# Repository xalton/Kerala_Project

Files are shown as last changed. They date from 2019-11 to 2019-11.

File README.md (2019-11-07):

# __PROJECT : refrigerant backpack__
*Team: Claire Chavigny, Carla Debarre, Ibrahim Khaled, Louise Gorioux*

> *A Myco-material backpack respecting the cold chain capable of carrying vaccines, allowing doctors to act while on the move to reach as many people as possible.*

## Project summary :

After many researches on the web, discussion with Indians, people from the medical sphere, our professors  and reflexions within our groupe, the project consists of a backpack capable of transporting vaccines, in an appropriate environment (2°- 8°C) over a six-hour period. Following the floods in India during last summer, poor healthcare has developed in the camps and diseases are spreading quickly. Moreover, if inhabitants want to be vaccinated they need to go to hospitals which are crowded in those moments. The project would be used during the camp period when infections are most common but also in everyday life to increase the impact of vaccination. 

The goal is to stop the spread of infection, reaching as many people as possible by giving them the opportunity to be immunized, thanks to the doctors on the field. Furthermore it will avoid the overload in hospitals. The project acts as a prevention in the camps after the disaster . The project aims to be more innovative than a cooling box by creating a myco-material refrigerant backpack. 

After several prototypes, tests and questioning, (cfr: process) we developed a backpack in polystyrene to find the best shape for the back and its thermal resistance (the ratio between thickness and thermal conductivity). In the bag stands a wood composite box (270mmx200mmx440mm) in which the 1O5 vaccines are located. Around the box are placed the eutectic plates. An unique assembly of straps is using all around the bag (it’s possible to use recovery material). 

The mycelium and the polystyrene have similarities regarding the thermal conductivity. It brings lightness to the bag. (cfr process).
To carry on our project, the backpack will be made by mycelium, which is the mushroom’s seed that could be developed by themselves. Thanks to it and the addition of substrate as sawdust, we are able to manufacture the material, called myco-material, biodegradable and one hundred percent ecological. For the development of the myco-material,  a cardboard mold’s need to be produced with the laser, as well as the box containing vaccines, from a file that we have made. 

The myco-material produces ten times lower carbon dioxide and uses eight times lower energy than the production of polystyrene foam. Its thermal conductivity is good enough to make it a good insulator completely ecological and biodegradable compared to polystyrene.

Concerning the production, Kerala arranges 22 fablabs and 3000 camps (disaster in august 2018) have taken their seats through the state. Furnishing two bags (210 vaccines) per camp means that every fablab should provide 270 bags. The web of fablabs in Kerala being dispersed, it would help us to send the bags to the various hospitals around. 

Regarding the time of production, we calculate that we need 5h beside the 30 days of myco-materials culture. The price of the bag is approximately 30 euros and total weights is 3.7kg.

We approached this project through the healthcare problem, that seemed important to all of us. There are many things still to be improved and we hope it will give idea and motivation to the NGO to develop a better version of it. We also wanted to enhance the agricultural crop by  using mushrooms and promoting innovative way of building that take care of the environnement. 

##  Storyboard :

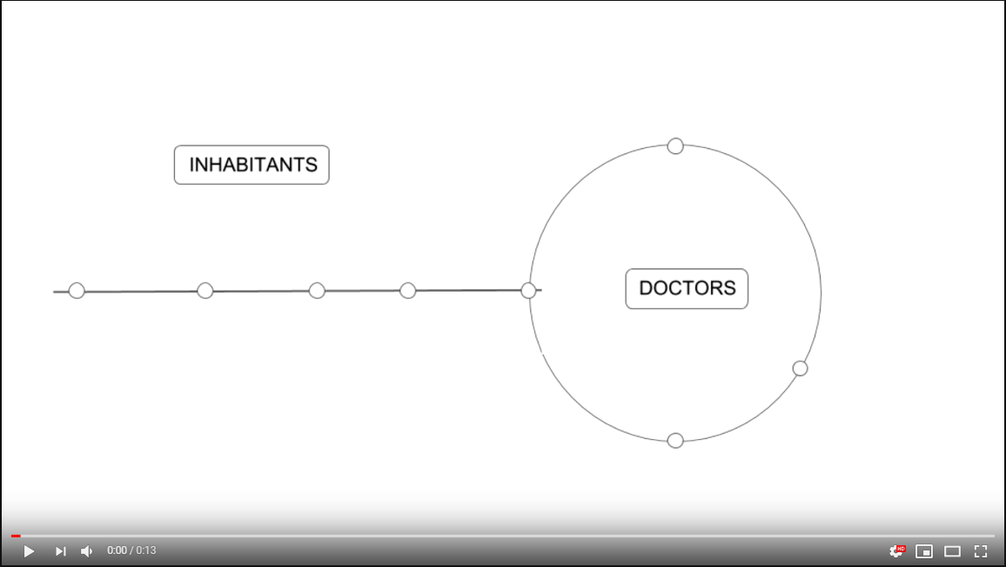
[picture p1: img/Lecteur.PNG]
Storyboard (https://youtu.be/2fGu3O8SxWQ)


##  Final prototype: 

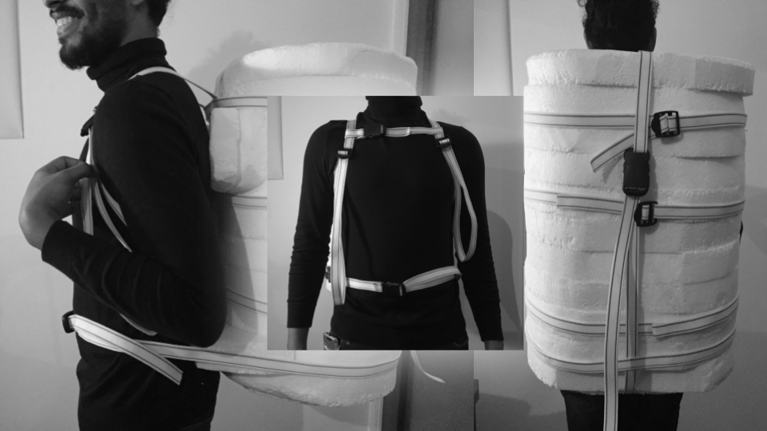
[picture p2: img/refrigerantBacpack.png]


## Tutorial :
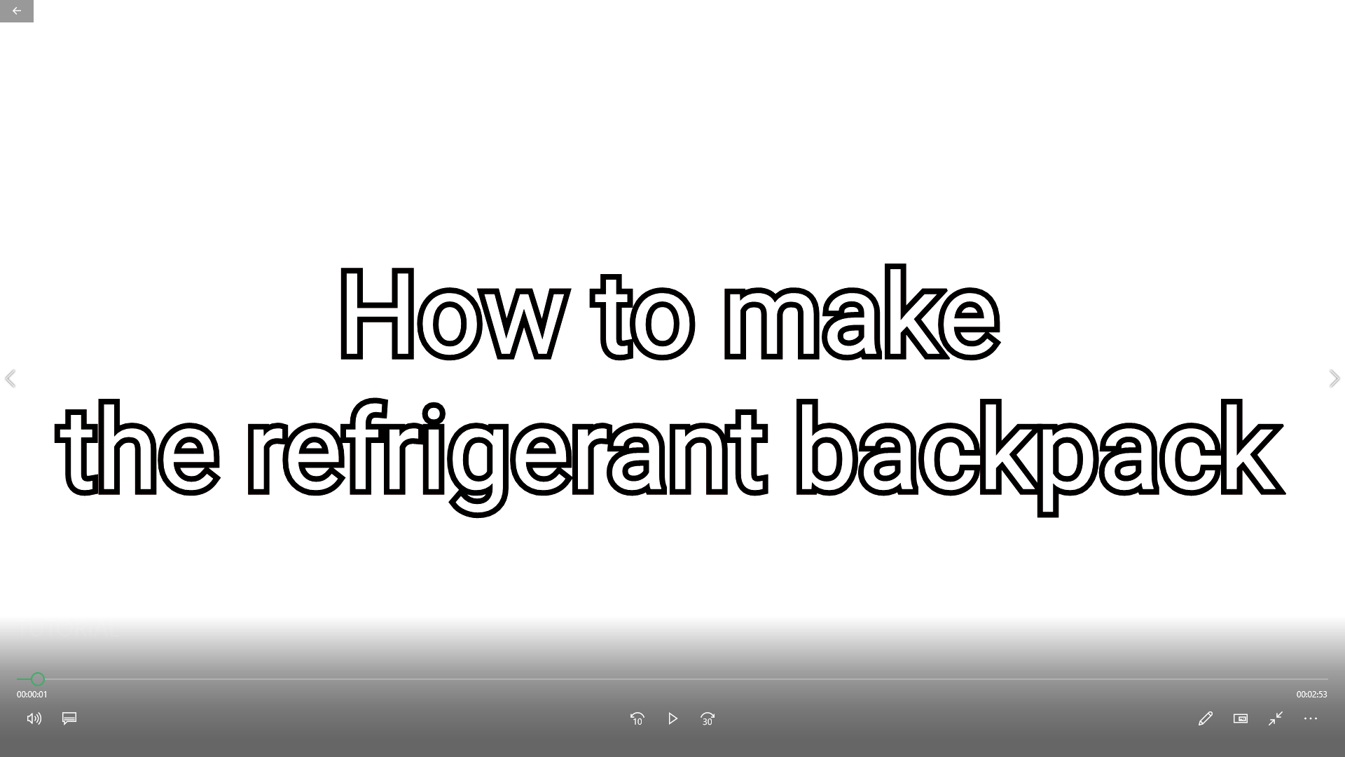
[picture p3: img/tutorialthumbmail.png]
tuto (https://youtu.be/IbsIk9dsDAU)


##  Bibliography :
- Contacts:
	- Pauline Kennes and Catherine Bachy at DWB Belgium

	- Michäël Gäthögö at DWB

	- Prithvi helped us as a local inhabitant
- Links:
	- [http://www.who.int/immunization/programmes_systems/supply_chain/optimize/Cooling_17july12.pdf](http://www.who.int/immunization/programmes_systems/supply_chain/optimize/Cooling_17july12.pdf)

	- [https://www.cdc.gov/vaccines/recs/storage/downloads/emergency-transport.pdf](https://www.cdc.gov/vaccines/recs/storage/downloads/emergency-transport.pdf)

	- [https://www.permafungi.be/projet/](https://www.permafungi.be/projet/)

	- [https://www.mediamatic.net/en/page/69393/mycelium-theorists-scientists](https://www.mediamatic.net/en/page/69393/mycelium-theorists-scientists)

	-	https://emergency.unhcr.org

	-	[https://motherboard.vice.com/en_us/article/pgazx8/the-house-that-spores-built](https://motherboard.vice.com/en_us/article/pgazx8/the-house-that-spores-built)

	-	[http://www.mycoworks.com/](http://www.mycoworks.com/)

	-	[http://ecovativedesign.com/](http://ecovativedesign.com/)

	-	[https://www.irit.fr/neocampus/images/stages/2018/Balthazar-Lesmie_Stage.pdf](https://www.irit.fr/neocampus/images/stages/2018/Balthazar-Lesmie_Stage.pdf)
	-   [http://www.cg43.fr/sites/cg43/IMG/pdf/guide_des_materiaux__isolants.pdf](http://www.cg43.fr/sites/cg43/IMG/pdf/guide_des_materiaux__isolants.pdf) 

	-	[https://www.netzsch-thermal-analysis.com/fr/materiaux-applications/isolation-thermique/polystyrene-expanse-conductivite-thermique/](https://www.netzsch-thermal-analysis.com/fr/materiaux-applications/isolation-thermique/polystyrene-expanse-conductivite-thermique/)
	-   [http://champignonscomestibles.com/clonage-culture-mycelium-carton-champignon?fbclid=IwAR3gGQV-I-8NpoABAhbPs69Wjr7dqdKYpgR8qhiwi3MI7uJcOvaIY5pMYXM](http://champignonscomestibles.com/clonage-culture-mycelium-carton-champignon?fbclid=IwAR3gGQV-I-8NpoABAhbPs69Wjr7dqdKYpgR8qhiwi3MI7uJcOvaIY5pMYXM)

	-	DUNCHEVA T., “Recycling : Mycology, Materials Science and Architecture”, AR521:Interdisciplinary University of Kent, 2013.

	-	JAMESON C., THOMAS T.J., WILLIAMS R., Mycelium Material Study, Studio Mur Mur Chicago, 2014.

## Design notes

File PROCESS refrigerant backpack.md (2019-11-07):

# PROCESS : refrigerant backpack

*Team: Claire Chavigny, Carla Debarre, Ibrahim Khaled, Louise Gorioux*

> _A backpack respecting the cold chain capable of carrying vaccines, allowing doctors to act while on the move and made from Myco-material._

## CONTEXT :

After disasters in India this August, the country has suffered of propagation of diseases following the poor hygiene conditions in the camps due to long wait surrounded by water. The emergency situation complicates the movement of citizens to hospitals, so many citizens do not have the opportunity to get vaccinated which amplifies the spread of diseases.

Moreover, after our first discussion with Michaël Gäthögö (an engineer at MSF), he told us that doctors don’t have a useful box to carry vaccines because of the uncertainty of the cold chain. In these conditions none precaution are established. 

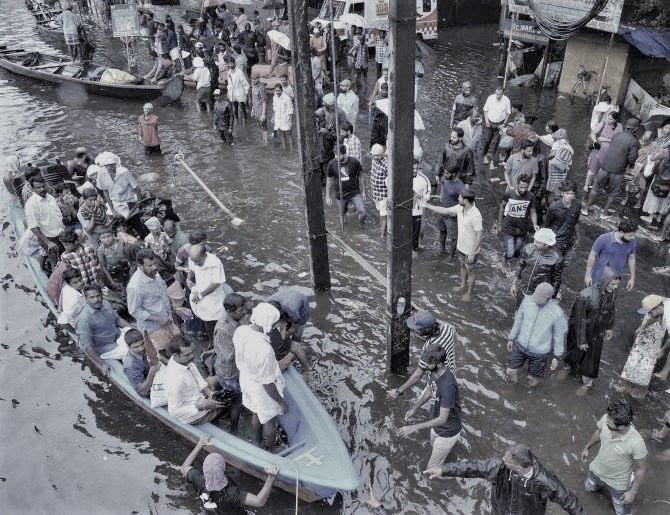
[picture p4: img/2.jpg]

*Disaster*
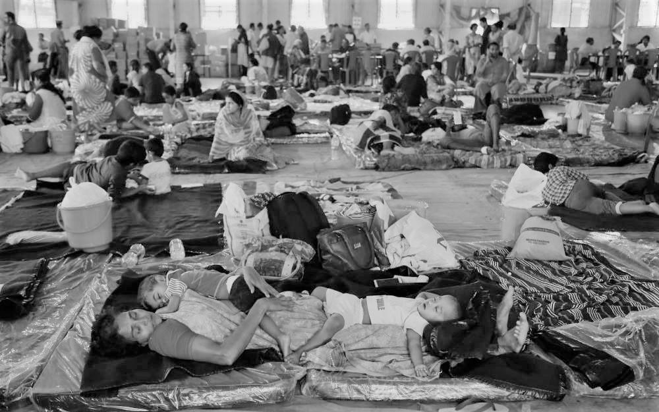
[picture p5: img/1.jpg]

*Camp* 

## GOAL :

We realized the importance of acting quickly on health. Furthermore, following several exchanges with Michaël Gäthögö, we concluded that a portable device was conclusive. Then we discussed the design of a cold chain refrigerant bag, capable of transporting vaccines. This seemed a relevant idea regarding the doctors, so that they can act while being on the move and then reach more people, but also to avoid the overload of hospitals.

## IDEAS-PROTOTYPES :

### FIRST IDEAS : 
Our initial project idea was a Peltier system with ventilation but we rapidly conclude that it will be difficult due to the complexity of the conception (electronics system with battery…) and the  price. 
Then we headed back to two differents options without energy: an evaporation system (as a “desert fridge”) and insulation one. 

### EVAPORATION SYSTEM :
After researches, we quickly understood that the evaporation one will be difficult due to the high weight ; sand and terracotta, so came the idea of a plastic box. Due to the high rate of humidity in India (over than 80%) this system won’t allow the constant temperatures required for the medical products. Which means that the evaporation system won’t work. 

With the aim of  the climatic conditions, researches on the insulation system as well as hospitals and camps positions, we have hypothesized that the bag has to respect the cold chain around 6 hours. Through the composition (heat source and thermal insulation) the insulation system should be able to maintain constant heat over a specified period of time. However materials composition has to be carefully thought. We decided to pursue on this way to deepen and try prototypes.  

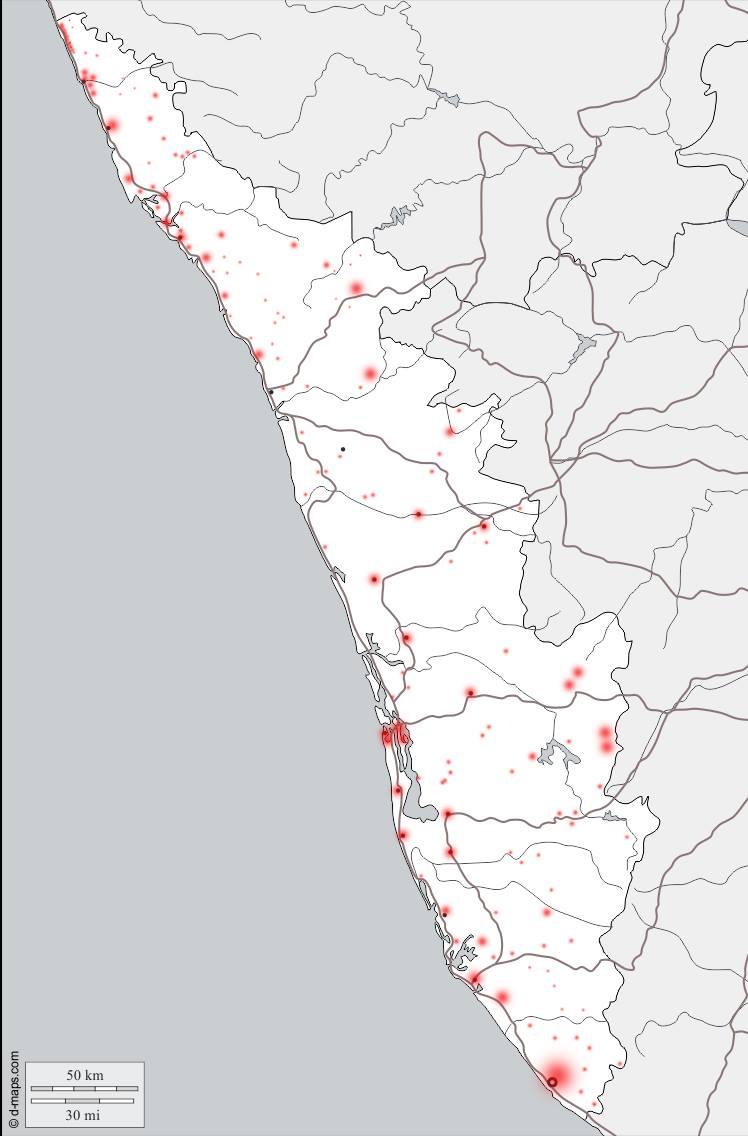
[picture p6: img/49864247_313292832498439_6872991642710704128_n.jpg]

*Positions of hospitals in this region*

### INSULATION  SYSTEM :
Our first prototype in Haugimont was made with polystyrene as insulation (2cm) and Plexiglas (5mm)  box to avoid the contact between the vaccines and the heat source (cold or hot) in order to prevent the liquid from freezing. The box, which has been cut with the CNC, in order to discover machines and try the first hypothesis. This recipient contains 75 vaccines and three eutectic plates of 500ml each (around -10°C). The first conclusion was that the Plexiglas is too fragile and the box is too heavy. Then we tried the system with a thermometer on a certain time, it reached the correct temperature (between 2-8°C) but not quickly enough. 

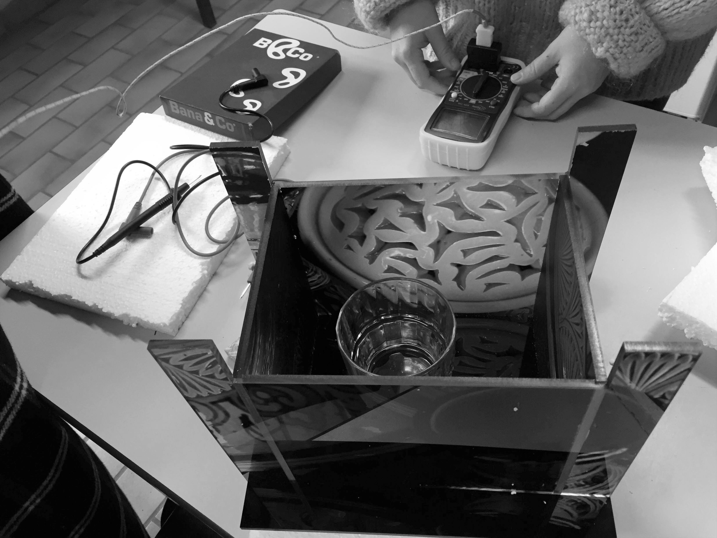
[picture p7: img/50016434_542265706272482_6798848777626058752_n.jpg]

*Prototype 1*
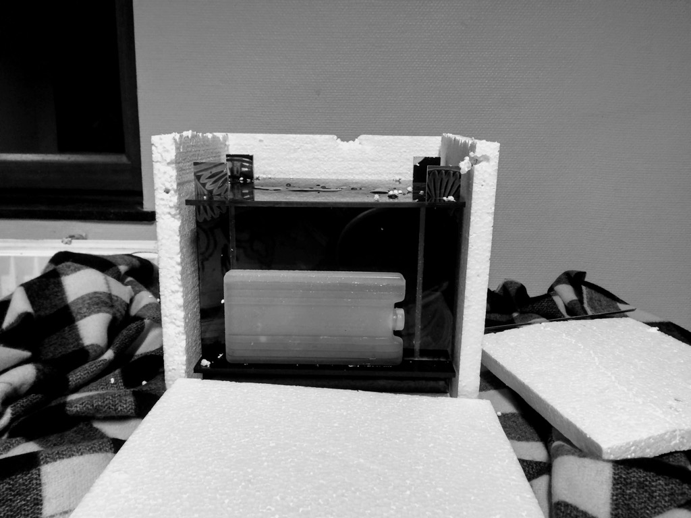
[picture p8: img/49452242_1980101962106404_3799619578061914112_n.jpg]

*Prototype 1-Eutectic plate*
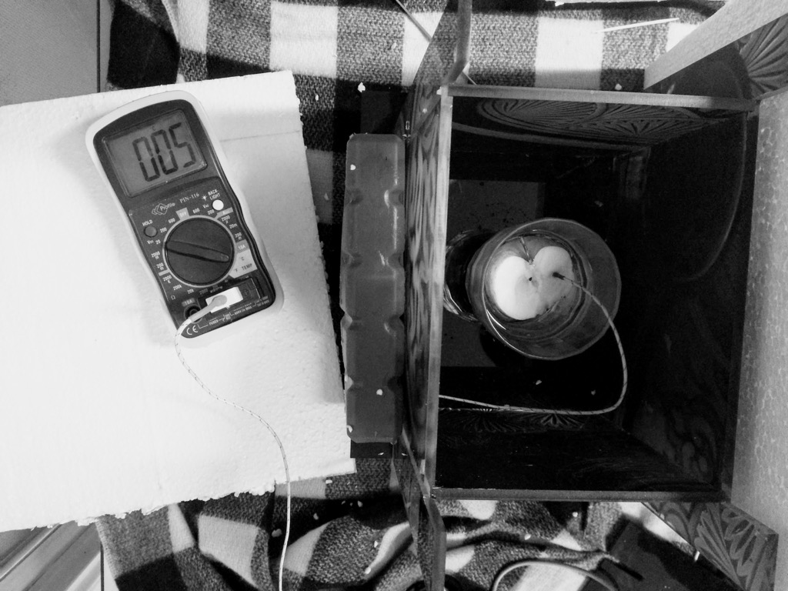
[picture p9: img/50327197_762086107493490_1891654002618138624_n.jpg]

*Prototype 1-Test*

After the first test, we concluded that the system works, to rise the conductivity and reduce the weight. We decided to make a second prototype with a lighter box. Using the same insulation’s system adding one more layer and a felt outside envelope to rise the performance. To avoid any perturbation  during opening the lid, we made slots in each of the two rubber layers (each slot is in different direction to decrease heat loss). After the experience on 8 hours, we noticed that the temperatures had passed below 0°C, the device is unreliable so we have to work on the temperature and the quantity of the eutectic plate which were both too high, the composition of the object and dimensions too. However the weight is appropriate.     

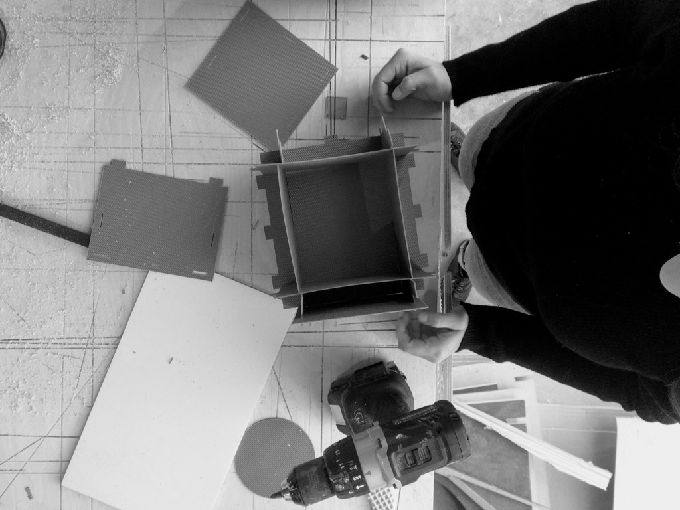
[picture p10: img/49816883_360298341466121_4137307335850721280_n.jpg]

*Prototype 2-Box*

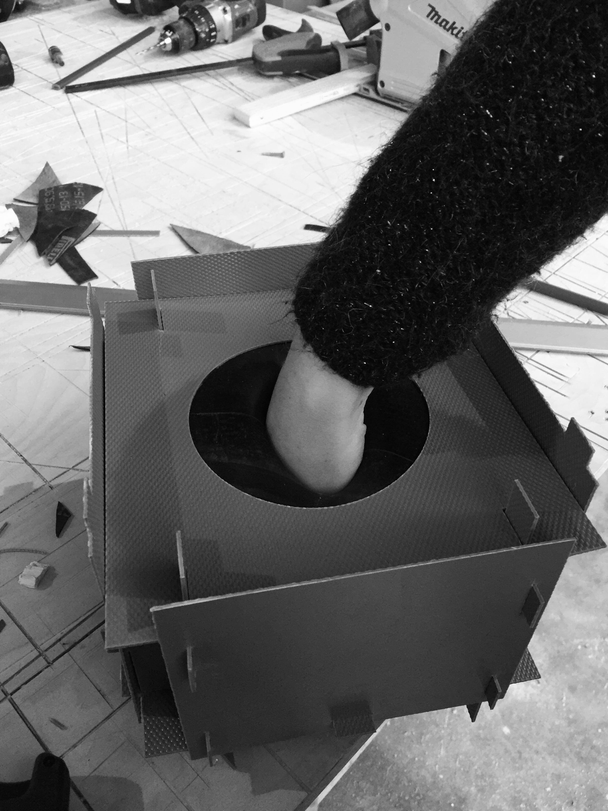
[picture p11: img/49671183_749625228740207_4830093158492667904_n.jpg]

*Prototype 2-Slots*

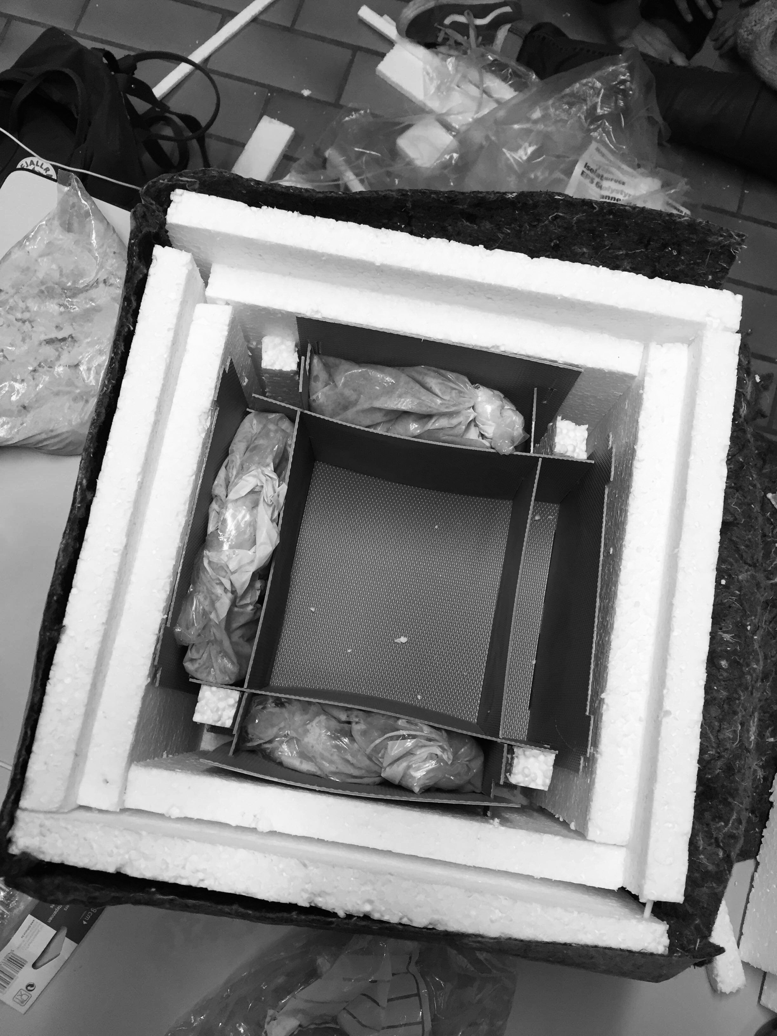
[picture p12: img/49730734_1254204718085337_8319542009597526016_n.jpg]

*Prototype 2-Inside de box with eutectic plates*

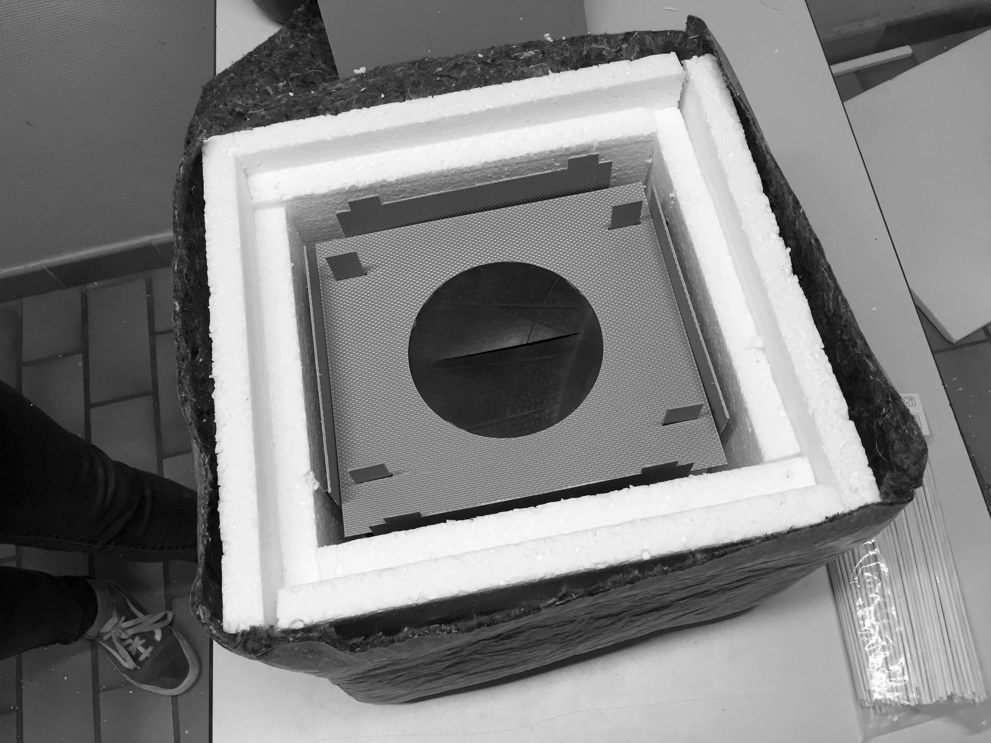
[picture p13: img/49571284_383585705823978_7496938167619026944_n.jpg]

*Prototype 2 - With insulant*

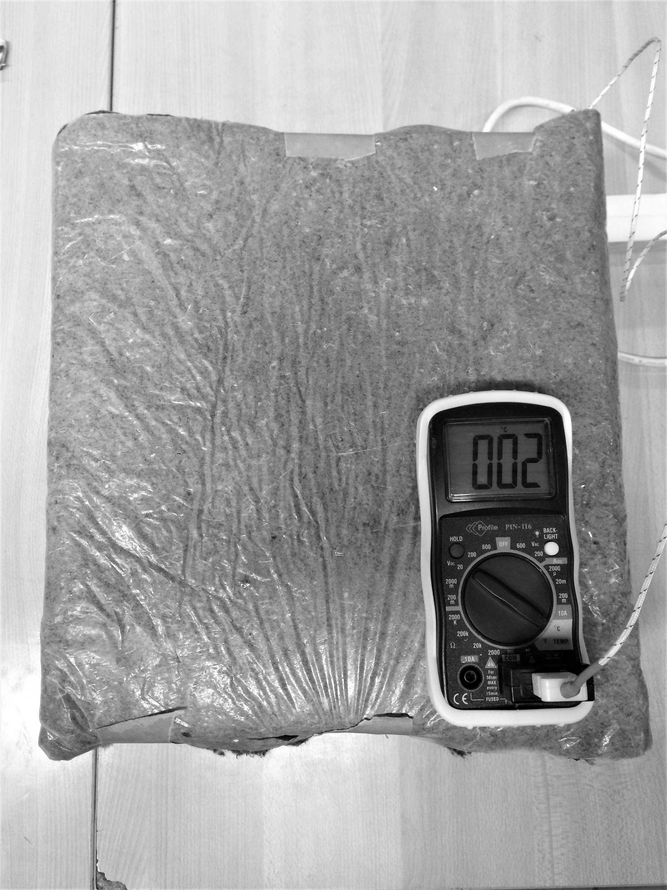
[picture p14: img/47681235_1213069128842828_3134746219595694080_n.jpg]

*Prototype 2- Test*

### IMPROVEMENT :

Following the week in Haugimont, we wanted to use local products to reduce the price of the bag. Further to some exchange with Prithvi Vesla (a contact living in Tamil Nadu, the province next to Kerala) we changed the two plastic boxes with one MDF box to reduce quantity of the material. We used tarpaulin instead of felt for the outside envelope to ensure the permeability of the bag during the transport. It will guarantee the permeability during transport. A new idea was to weld the tarpaulin with the polystyrene in, to protect it. 

Moreover we thought about the coconut fiber which is popular as an insulation and it’s an abundant resource but unfortunately we can not make something too heavy. To try the thermal resistance (the ratio between thickness and thermal conductivity) we reduced the thickness of the polystyrene (2cm). After two differents tests on 6 hours, the results were not good enough and have taken too much time to reach the right temperature. So we have to increase its thickness and test it again to assure the reliability. 

#### FIABILITY OF THE BAG : 
Concerning the first test, 4 eutectics plates of 500ml each were between -3° and -1°C. It is only after 40 minutes that the air inside the box reached the temperatures required and the minimum ambient fluctuated around 7°C. Moreover, after 2 hours the temperature exceed 8°C. That result was not sufficient.

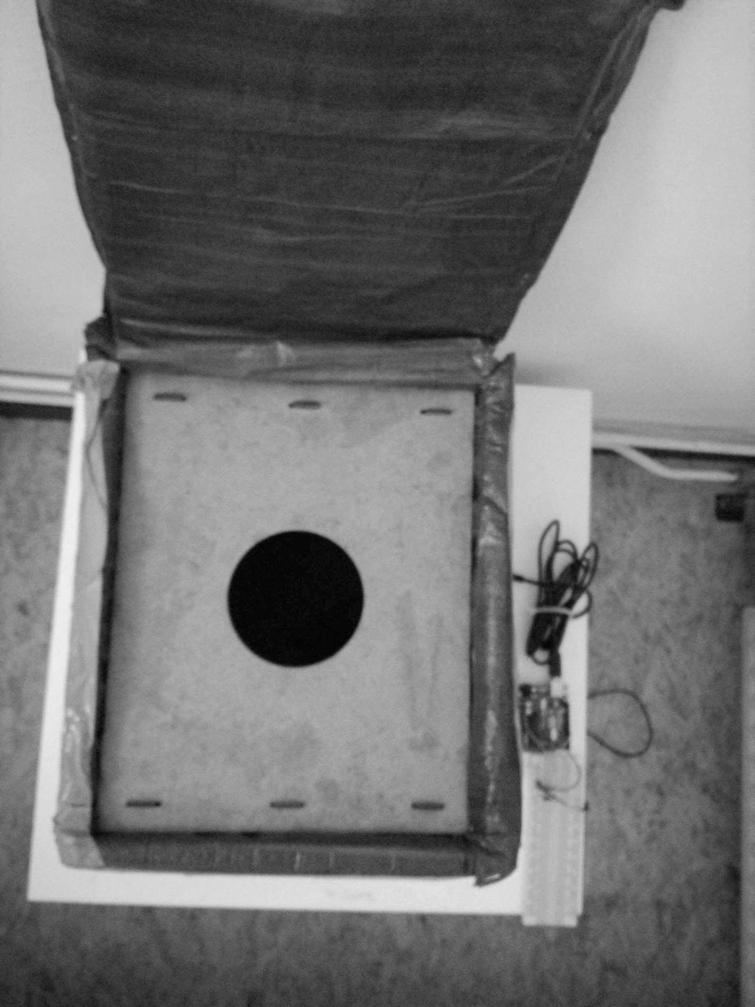
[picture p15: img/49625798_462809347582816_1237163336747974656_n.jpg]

*Prototype 3 - From above*

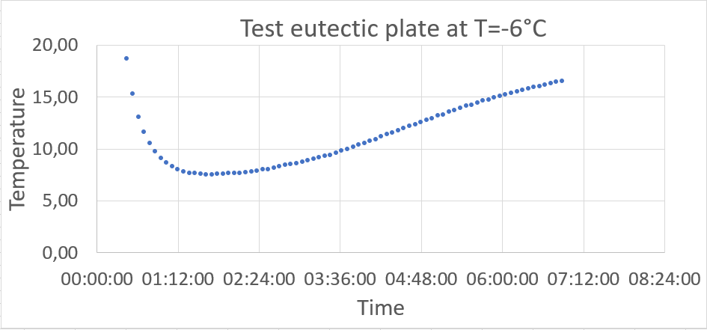
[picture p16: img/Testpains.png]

*Prototype 3-Test with 4 eutectic plates at T = -6°C*

For the second test, we tried the same amount of eutectic plates but colder ( -6°C and -9°C). We noticed an improvement compared to the previous one but it still not relevant enough. It takes too much time to achieve an ideal temperature as well as the stability. We had to reconsider the problem and think out of way. How could we improve the box’s shape and make it more ecological by using a new material.

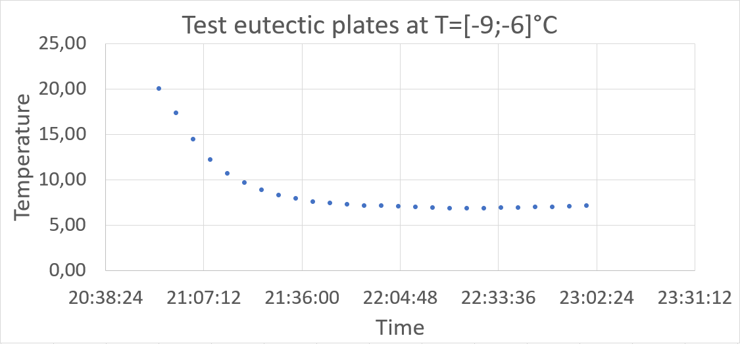
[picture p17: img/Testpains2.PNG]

*Prototype 3-Test 2 with 4 eutectic plates at T = [-9;-6]°C*

### INNOVATION :

After many reflexions and researches we wanted to create a project more inovant and more comfortable for the back. We discovered the mycelium,  the vegetative part of mushrooms that becomes hard as a rock and insulator while dehydrated. It has many great characteristics as light, resistant, waterproof, flammable and floating. Some people have already built structures (design bricks or atypical and unique shape) or created objects (bowl, chair, lampshade) and it showed off its success. 

#### INSULATING POWER OF THE MYCELIUM : 

-   **Thermal conductivity (W/(mK))** : It characterizes a material’s ability to drive the heat. The lower this value, the more insulating the material. According to the French RT2012 standards, a material is considered as insulating if its thermal conductivity lags behind 0,065 W/(mK). In comparison, the polystyrene ‘s thermal conductivity is 0.039W/(mK) at 24°C. (Demonstrated by Netzsch)

-   **Thermal resistance (m^2K/W)** : it defines the material's capacity to insulate for a certain thickness. It is the ratio between the material’s thickness (meter) by the factor of thermal conductivity λ. The higher the heat resistance, the more insulating the wall.

-   Lesmie BALTHAZAR obtains,throughout his study, a value of 0.058 W/(mK) for a substrate over chenevotte via thermal drying.(average density  0.113g/cm^3)

We concluded that the mycelium is a good insulator even though it is less performant than polystyrene. From results of the Polystyrene bag, it’s possible with the mycelium to achieve  similar results considerate the thermal conductivity and a lighter weight ( according to the board below ) :


*Table- Comparaison between polysteren and mycelium*

**Remark** : Regarding the outside temperature and its influence over the material’s thermal conductivity, a study lead by Netzsch shows that there is a difference of less than 1% between the value of thermal conductivity measured at 10°C and 24°C. Given the fact that the mycelium ‘s thermal conductivity isn’t far from the polystyrene’ s one, we can assume that its value at 20°C and at 30°C won’t be any different. Unfortunately, because of a lack of time and samples, we couldn’t conduct our own thermal conductivity’ s measures; this is why we made assumptions. 

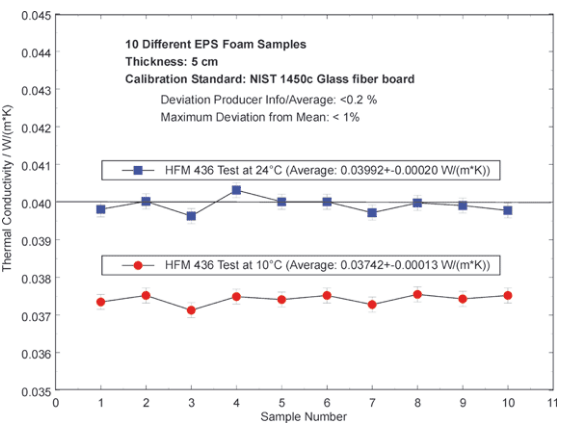
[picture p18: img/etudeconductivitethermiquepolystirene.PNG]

*Graphe of deviation from mean of thermal conductivity for polystyrene*

#### HOW TO DO IT ?
It’s possible to cultivate mycelium from pieces of mushroom and various substrates in sterilized boxes. To try this new material we have attempted to cultivate six different ways to be able to assert the quickest.  

- N°1:  Button mushroom + cardboard 
- N°2: Oyster mushroom + cardboard
- N°3: Button mushroom + walnut shell +  flower 
- N°4: Oyster mushroom + walnut shell +  flower 
- N°5: Button mushroom  + coffee ground + cardboard
- N°6: Oyster mushroom + coffee ground + cardboard

After two weeks into the dark, the oyster mushroom and some coffee ground were the best (n°6). Following this step, three more steps are essential to produce the insulated myco-material : the inoculation, the incubation and the dehydration. 

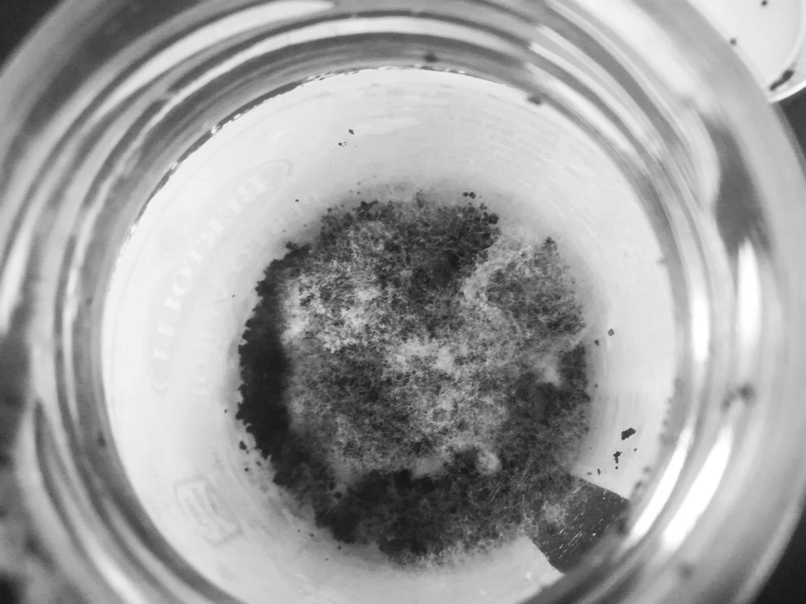
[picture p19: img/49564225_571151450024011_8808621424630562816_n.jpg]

*Mycelium*

Furthermore, a cardboard mould is essential for myco-material’s development which is the incubation. To create the mould, we used the sliced technique, using the laser , then we covered it with paper and added plastic to facilitate the adhesion of mycelium. The use of a heat-shrinkable plastic will be easier and quicker. Our mistakes were that we didn’t test the shape of the back on us and we didn’t realize that we needed to open the mould to process the dehydration step. Moreover the thickness of the cardboard (2mm) to make the mould was too thin so not enough robust to join all pieces. 

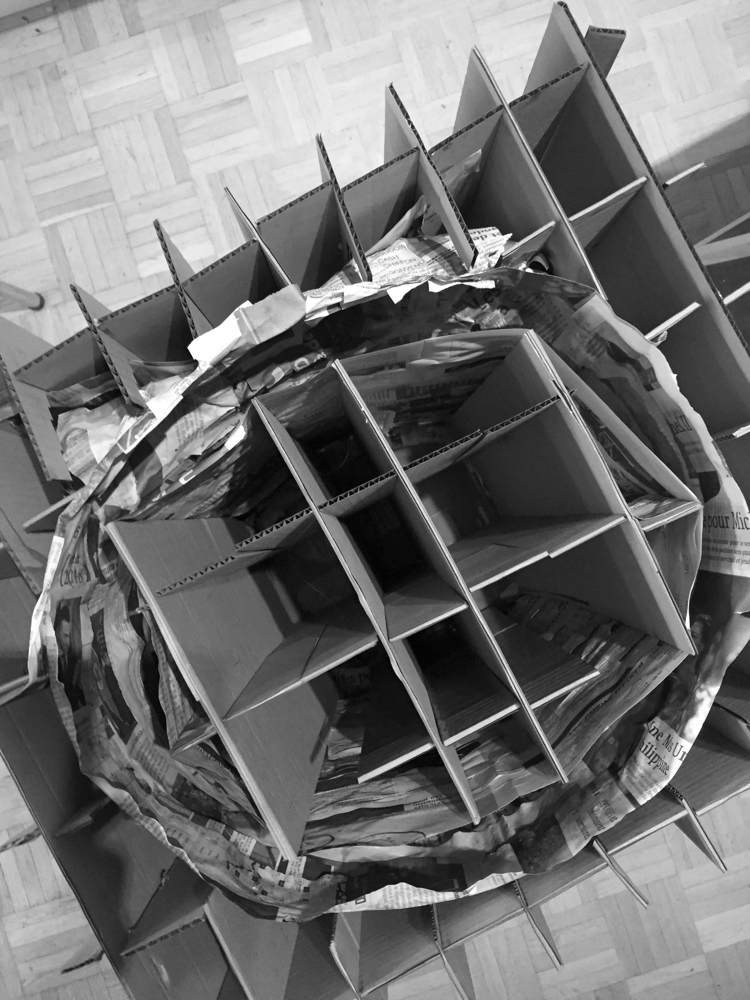
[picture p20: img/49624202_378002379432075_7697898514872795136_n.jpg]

*Mould*

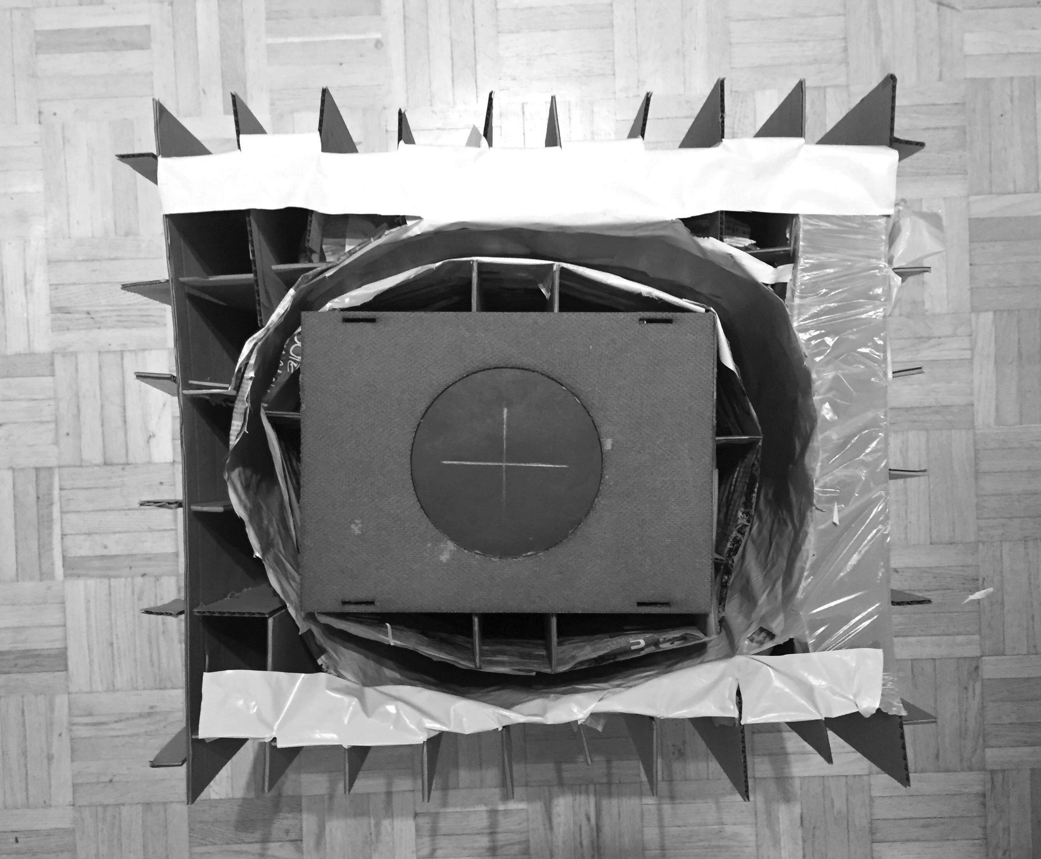
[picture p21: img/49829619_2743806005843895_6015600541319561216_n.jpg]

*Mould- From above*

### WORK ON THE BAG’S SHAPE : 
After researches on different composition of trekking bag and discussions with our professors about the ergonomic of the bag, we decided to create a bag in polystyrene because of the facilities to sculpt and compare directly with the reality. Moreover we have used modeling pastes which can take a specific form from the body. We have tried 3 different shapes. 

First, we tried a shape that covered all the length on each side of the back but we quickly stopped designing it because after several fittings we understood it wasn’t necessary to put that much.

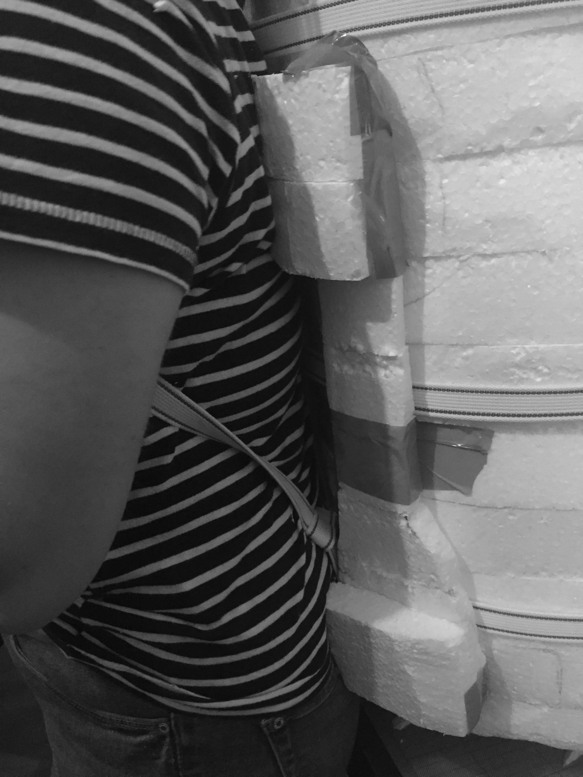
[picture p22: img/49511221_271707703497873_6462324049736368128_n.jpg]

*Test0-Shape who covered all the length*

Secondly, we tried a device that surrounds the waist and we noticed that it really helps for the back‘s support. Before finding the right form, we used paste to take the appropriate shape. These modules will be part of the mycelium mould and are enclosed by the adjustment ’s straps.

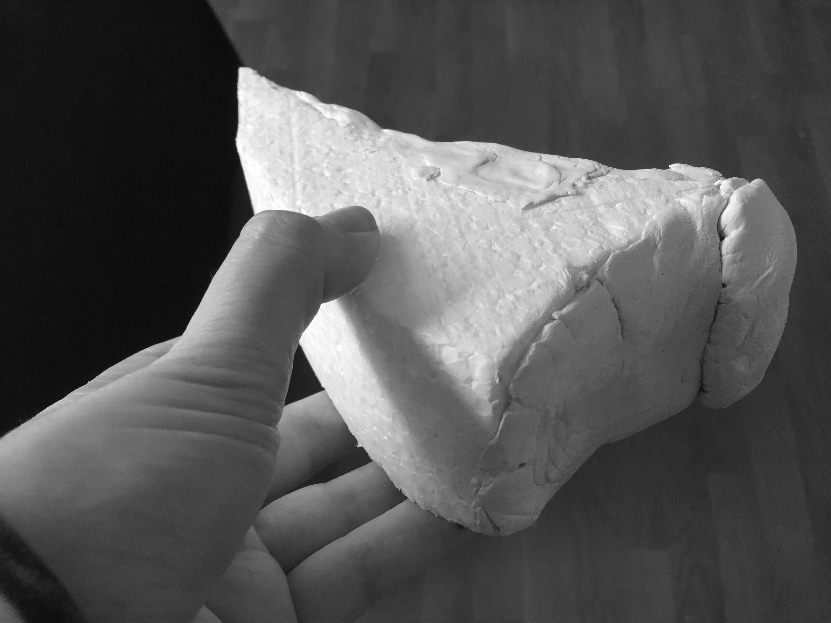
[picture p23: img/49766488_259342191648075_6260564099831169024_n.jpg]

*Test1- Shape for the lower back* 

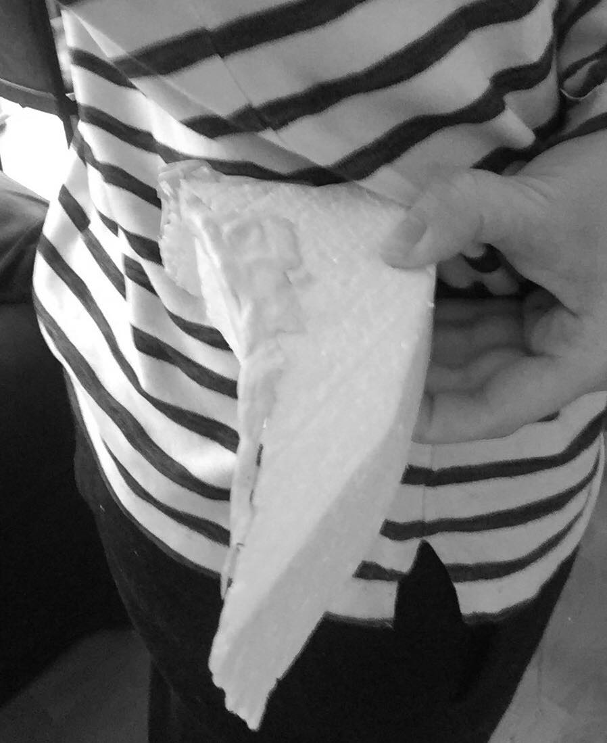
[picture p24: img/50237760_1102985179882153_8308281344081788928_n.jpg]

*Test2- Shape for the lower back* 

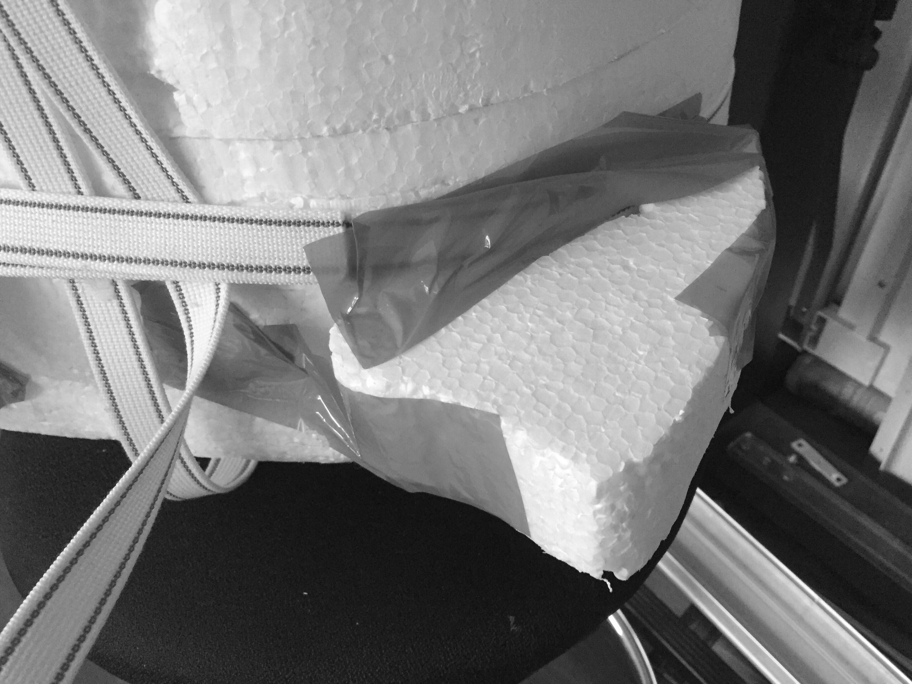
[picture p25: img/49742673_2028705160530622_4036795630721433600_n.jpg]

*Test3-Test- Shape for the lower back*

Once we were satisfied, we focused on the upper back. We tried different shoulder blade ‘s shapes. We first tried something rounded that touched the bones but it wasn’t comfortable because of pushing the upper back forward. It was disturbing the free movement of the arm. 

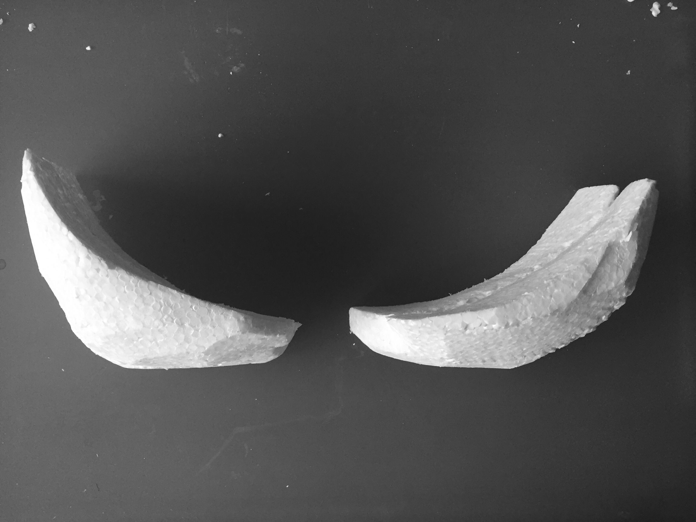
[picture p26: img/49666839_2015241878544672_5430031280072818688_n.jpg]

*Test1-Shape for upper back*

We headed to something thinner, covering the outer part of the shoulder blade. Same as before, we used the modelling paste to approach the best as we can the right shape. 

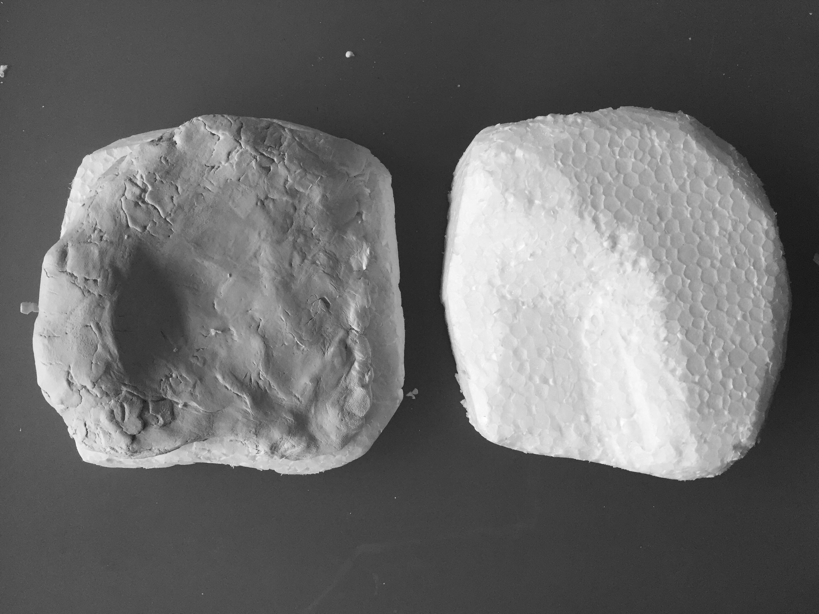
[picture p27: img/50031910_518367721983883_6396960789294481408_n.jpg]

*Test2-Shape for upper back*


*Test2- Other view*


*Test2-On the model*

We ended up increasing the outer part, because it felt more comfortable and supporting. After some adjustments, we were pleased with the results so we made it the final version. 


*Final version*

Concerning the straps, there are 4 different types. The vertical straps and the loops are joined together by tensioners. The chest and waist straps are fixed together with clip buckles. In order to avoid any disturbance of the straps we crossed it, giving them a direction holding by three more horizontal straps on three differents levels. 


*Straps plan*


*Straps in real*

#### FIABILITY OF THE BAG : 
We started a new temperature test after 3 hours of refrigeration of the 9 eutectic plates of 200ml each (with temperatures varying from -8°C to -4°C). We observed a drop of the temperature after inside the box that was expected (after 10 min) because it will ensure the rapid departure of the doctors from the hospitals. The box answered the required criteria (between 2°C-8°C) on a 5 hours period. 


*Final prototype-View of the box from above*


*Final prototype-Test eutectic plates at T=[-8;-4]°C*

We wanted it to last a bit more so we started a new test and added 5 more eutectic plates of 200mL But it reached zero too quickly so we stopped it. Here are the results :


*Final prototype-Test2 Failed*

We then decided to reproduce the test but with an initial temperature (of the eutectic plates) around -3°C and 0°C.


*Final prototype-Test3 eutectic plates at T=[-3;0]°C*

The results were a little bit different. At the beginning, the temperature dropped slower than the prototype n°4 test 1 (in 15 min). However there was a better stabilisation of the temperature over the 5 hours. Concerning all the test, the cold chain was respected over 5h30 maximum. 

Finally, following the previous results,there are two trends in our graphs. In the first time of a decline. Firstly, an exponential decay of the temperature to a global minimum and then a linear trend growth. From this observation, adjustments can be made to derive a model whose parameters are:

- Minimum temperature required (T_0)

- Parameter related to the cooling rate (alpha)

- Slope of the linear part related to the temperature increase (beta).
Parameter that affects the cooling rate (related to material properties)

*Final graph-Comparison between our test and the model which represent the theoretical expected result*

we remark that the eutectic plates’ s number affect the duration in which the box stays between 2°C and 8°C. The temperature of the plates affect the minimum temperature that the box will reach. 

In order to improve the system, one could consider increasing the volume of insulation that would be in Mycelium and therefore do not increase enormously the mass of the bag. In addition, it would be necessary to find the best configuration of the eutectic plates for its influence on the parameters of the model. Finally, the recovery of materials should be optimized to reduce the cost of producing the bag.

*The refrigerant backpack is ready !*

We approached this project from the point of view of health, since this problem seemed to us all to be really important. There is still a lot to improve but we hope that it will give many ideas and motivation to NGOs to develop a better version. We also wanted to support agricultural production by promoting mycelium cultivation and methods of innovative and conscientious construction of the environment.

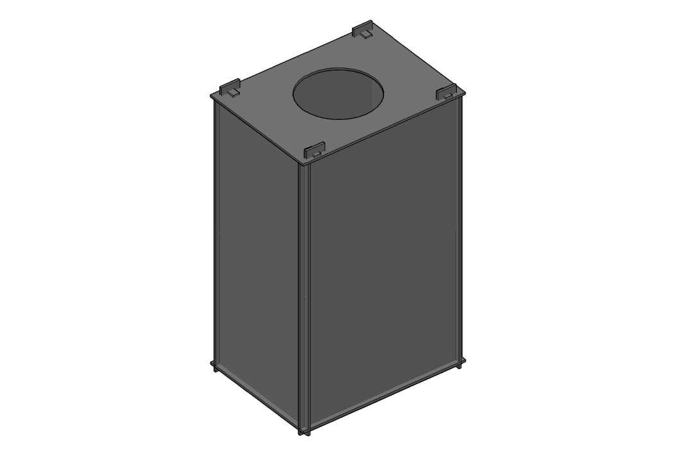
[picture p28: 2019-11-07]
img/box.PNG

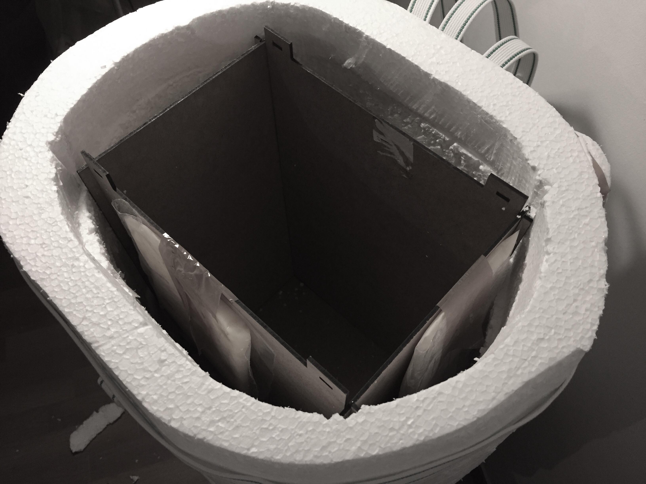
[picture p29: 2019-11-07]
img/49753126_552329385266084_2562119747806167040_n.jpg

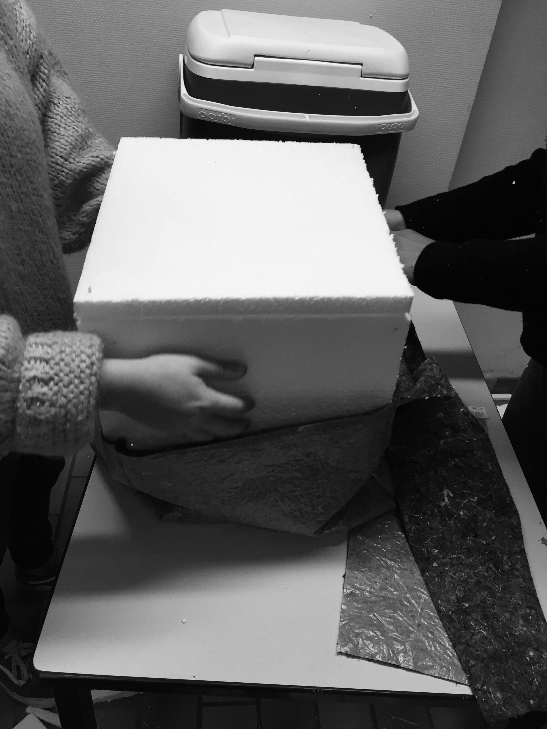
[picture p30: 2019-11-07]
img/49535876_320220991955085_5985407157451882496_n.jpg

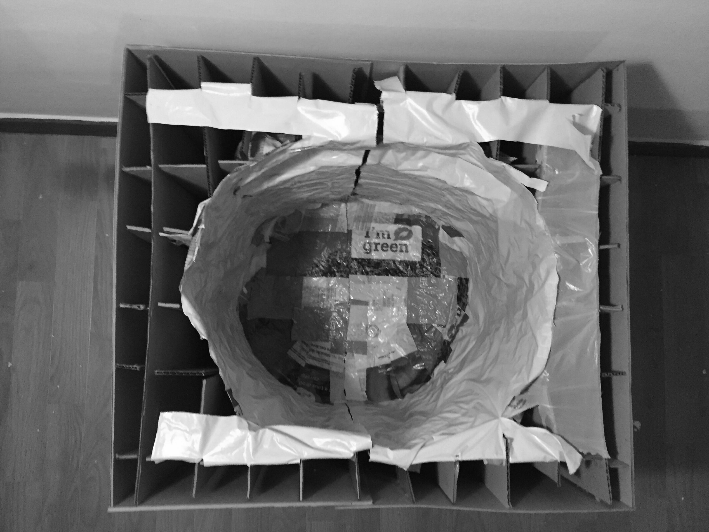
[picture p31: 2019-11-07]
img/49728045_1462775130526253_1488204776494596096_n.jpg
